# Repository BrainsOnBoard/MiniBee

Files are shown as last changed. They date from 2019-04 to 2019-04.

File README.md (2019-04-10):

# MiniBee Design files
Design files and instructions for the Brains On Board MiniBee quad rotor platform

## Components:
- Diatone Grasshopper 160 Frame
- Airbot Asgard/Asgard32 Flight Controller (Asgard32 has a barometer if required)
- 4 x EMAX RS1106 II motors
- DYS 3020 Propellers
- Raspberry Pi Zero W
- Raspberry Pi Zero camera (50 degree)
- Macro lens (e.g. https://amzn.to/2I5PW7b)
- Bubblescope 360 panoramic lens or other hemispherical mirror
- Adafruit BNO055 Orientation Sensor or other
- MicroUSB connector
- XBee3 2.4Ghz
- Many M2 7mm hex screws
- 6x M2.5 25mm nylon bolts and nuts

## Step 1: mount the motors
There are four M2 screws needed per motor. At this point the optional landing struts that allow VICON reflective trackers to be mounted can be affixed below the motors and frame, if required.
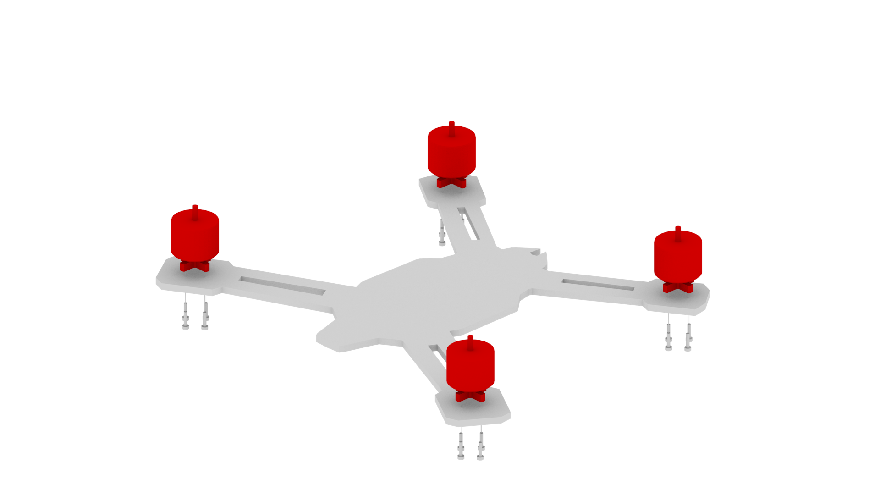
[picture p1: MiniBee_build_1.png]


## Step 2: solder motors to Asgard
The Asgrad will be oriented upside down from default to make the build work better. This means that the STM32 should be on the TOP. Rather than adjust the Flight Controller (FC) mixer a lot we can simply wire the motors to the opposite side of the craft. Note that the middle wire of the motor ALWAYS goes to the middle pad of the FC ESC, and the two other wires, if switched, will simply reverse the motor direction. The BetaFlight Configurator can be used to test the motor direction before fixing the FC in place - note the warnings given and don't attach props while testing!
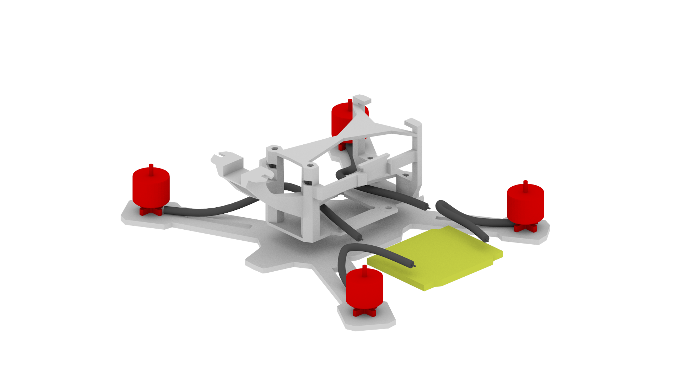
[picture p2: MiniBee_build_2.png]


## Step 3: vibration mount the Asgard
Rubber o-rings should be used between each of the layers to give good vibration damping. The nuts of the nylon bolts should be loosely tightened. After you are happy, use pliers or scissors to snip the excess nylon bolt.
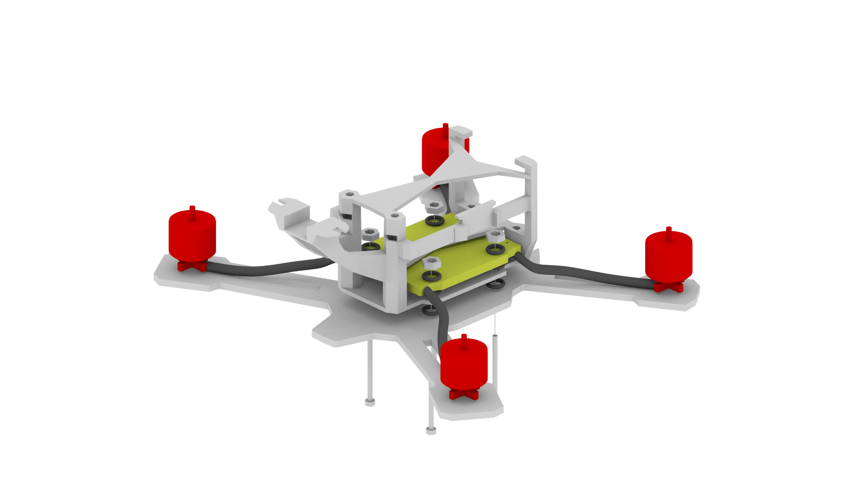
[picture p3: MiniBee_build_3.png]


## Step 4: mount the Pi and solder the orientation sensor 
The orientation sensor should be wired as in the Adafruit guide [here](https://learn.adafruit.com/bno055-absolute-orientation-sensor-with-raspberry-pi-and-beaglebone-black/hardware). The Pi is mounted by slipping it under the notches at the back of the structure, then pushing it down at the front and lining the holes with those on the structure.
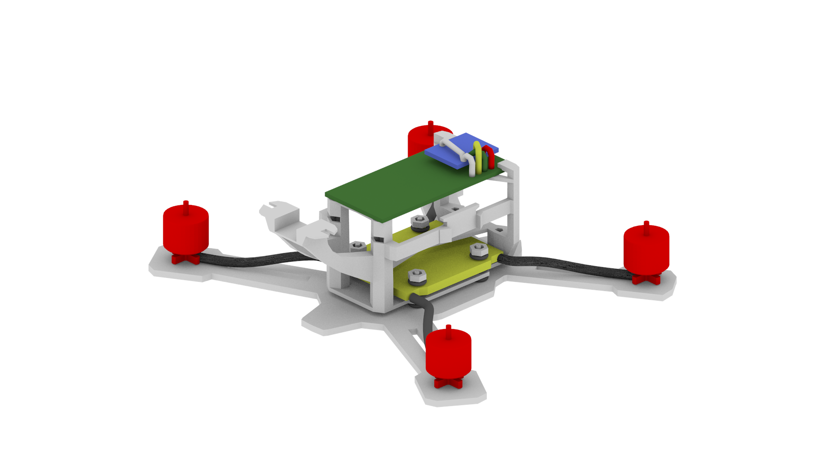
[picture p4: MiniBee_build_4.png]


## Step 5: mount the camera and lens
The lens should push fit into the camera structure as shown. The camera should be trapped between the camera structure and main structure. Nylon bolts and captive nutes secure the structures together at the neck, with the option of two smaller nylon screws (M2 is best) at the head either side of the lens.
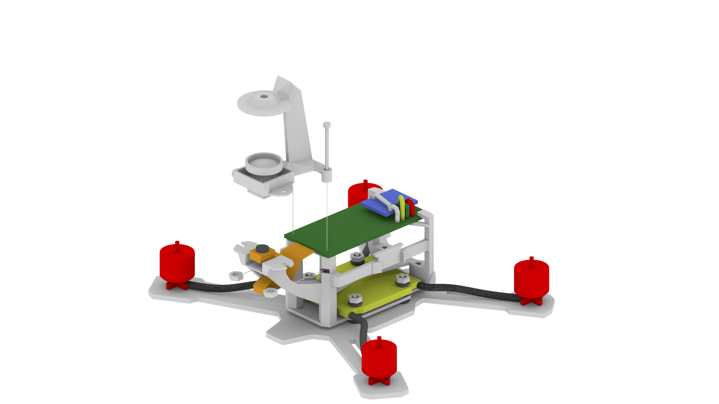
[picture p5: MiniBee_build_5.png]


## Step 6: mount the mirror
The mirror can e removed from the bubblescope by snapping the stem of the scope and working the stem until it disconnects. At this point the remaining peices will slide off leaving the mirror with a mount hole through the centre. Fix the mirror onto the top of the camera structure using a nylon bolt and nut.
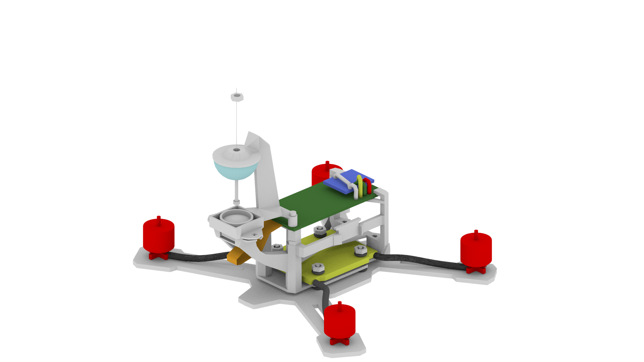
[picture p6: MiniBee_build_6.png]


## Step 7: connect the XBee3 module
The best way to connect the XBee3 to the Asgard is by purchasing a JST-1.0 4pin pre wired cable, and then soldering the ends onto teh MiniBee. The required connections are TX, RX, 3.3V power and GND. IMPORTANT: UART6 of the Asgard is the only one that can supply 3.3V powwer, and you must break the trace on the jumper pads that default the power to 5V and resolder for 3.3V, as per the Asgard information sheet [here](https://i.pinimg.com/originals/00/42/5b/00425ba4a4a2082930bc3ae4fa60683c.jpg). Make sure to test the volteage with a multimeter prior to connecting the XBee3 or you will destroy it!
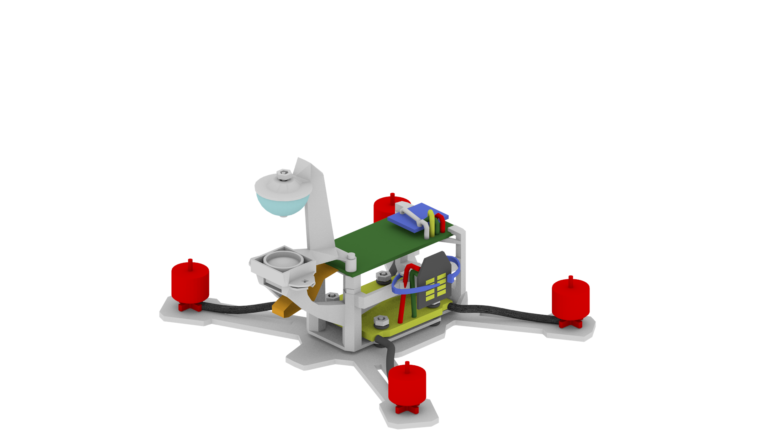
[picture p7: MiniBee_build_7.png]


## Step 8: power the Pi
The next step simply involves connecting power to the Raspberry Pi Zero W. This can be done from the Asgard MicroUSB port using a patch cable, or by soldering a MicroUSB connector for 5V and GND to the corresponding pads on the Asgard.

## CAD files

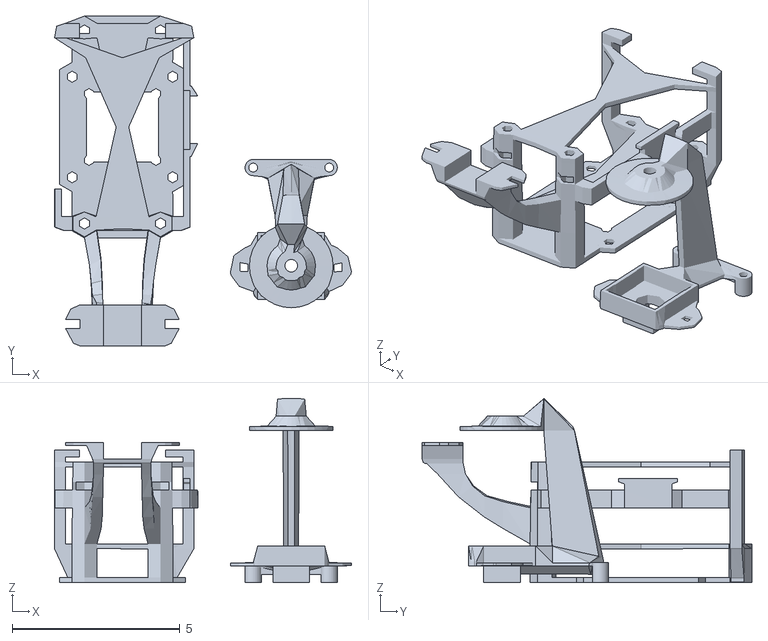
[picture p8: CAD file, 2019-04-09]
MiniBee_structure.stl
8.87 x 9.85 x 5.50

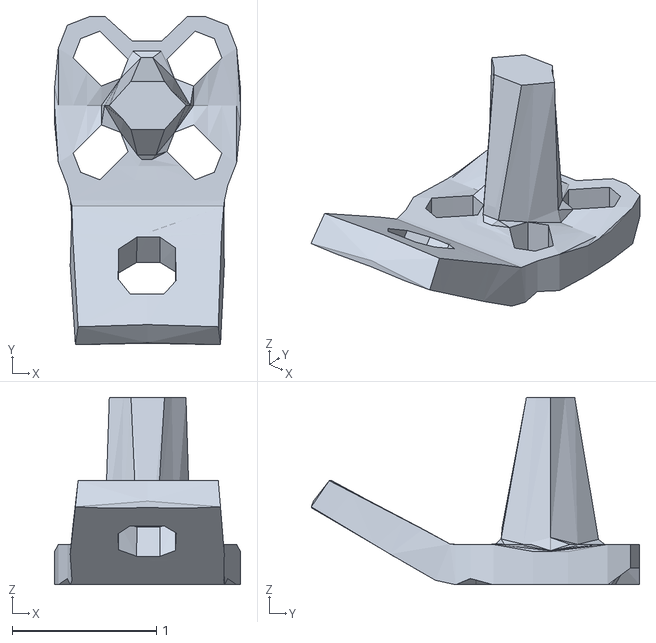
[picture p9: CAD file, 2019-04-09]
MiniBee_landing_struts.stl
1.29 x 2.28 x 1.30
